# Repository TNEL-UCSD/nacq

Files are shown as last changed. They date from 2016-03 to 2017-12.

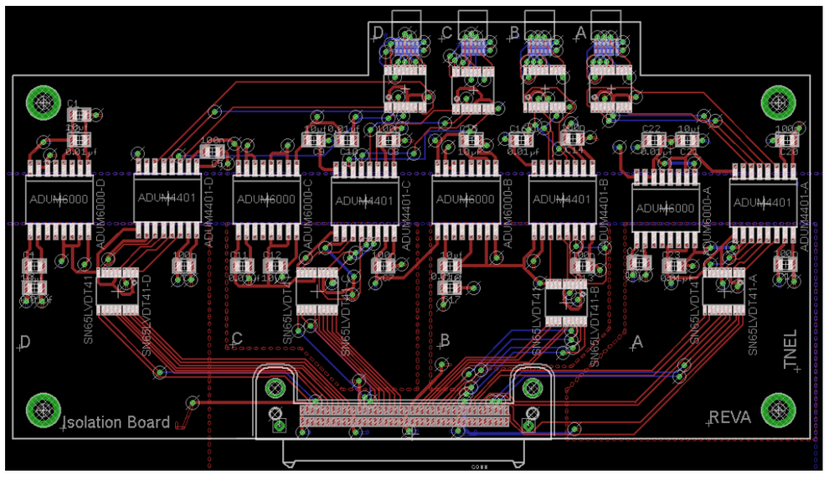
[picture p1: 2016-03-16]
cases/NACQ Case/isolation board.png

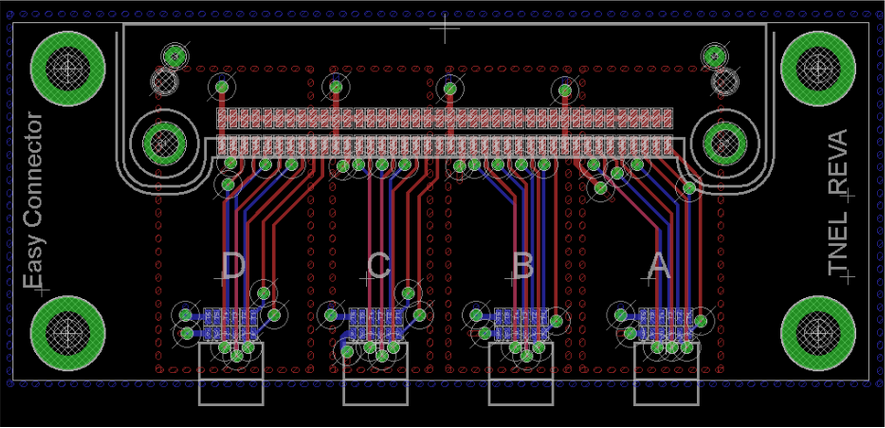
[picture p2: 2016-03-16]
cases/Easy Board Case/easy connect.png

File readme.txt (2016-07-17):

Overview:
Design files for a electrophysiology (ephys) recording tailored for the clinic. Our system is based on Intan technologies (intantech.com). 

If any of the materials are used, please cite:

J. Hermiz, N. Rogers, E. Kaestner, M. Ganji, D. Cleary, J. Snider, D. Barba, S. Dayeh, E. Halgren, V. Gilja "A clinic compatible, open source electrophysiology system." 2016 38th Annual International Conference of the IEEE Engineering in Medicine and Biology Society (EMBC). IEEE, 2016.

Included in this system are:

-Power Isolator (nacq/pcbs/Isolation Board)
-> Provides isolated power to Intan headstages. Can support up to 256 channels.

-Easy Board (nacq/pcbs/Easy Board)
-> Adapter for isolator board to intan spi cables

-Flex Adapter (nacq/pcbs/Flex Adapter)
-> Adapter that accepts flat flex cables (FFC) and plugs into headstages (RHD2132 and RHD2164)

-NACQ Case (nacq/cases/nacq)
-> Enclosure for neural acquistion hardware (power isolator and RHD2000)

-Easy Board Case (nacq/cases/Easy Board)
-> 3D printed case

Flex Adapter Case (nacq/cases/Flex Adapter)
-> 3D printed case

Intan Headstage Cases (nacq/cases/Intan Headstages)
-> 3D printed cases for RHD2164

NACQ Software (nacq/software/nacq)
-> Software to acquire and record data. Runs only on Windows 7+ systems.

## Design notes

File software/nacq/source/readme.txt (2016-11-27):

Slight changes made to intantech.com source code found on:
http://intantech.com/files/RHD2000interface_source_code_v1_5.zip

These changes allow RHD2000 USB Board to interface to the headstage through the isolators

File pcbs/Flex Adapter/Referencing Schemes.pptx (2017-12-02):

## Referencing Schemes

## Options

1. External reference
2. Device reference

## External reference

Front Side

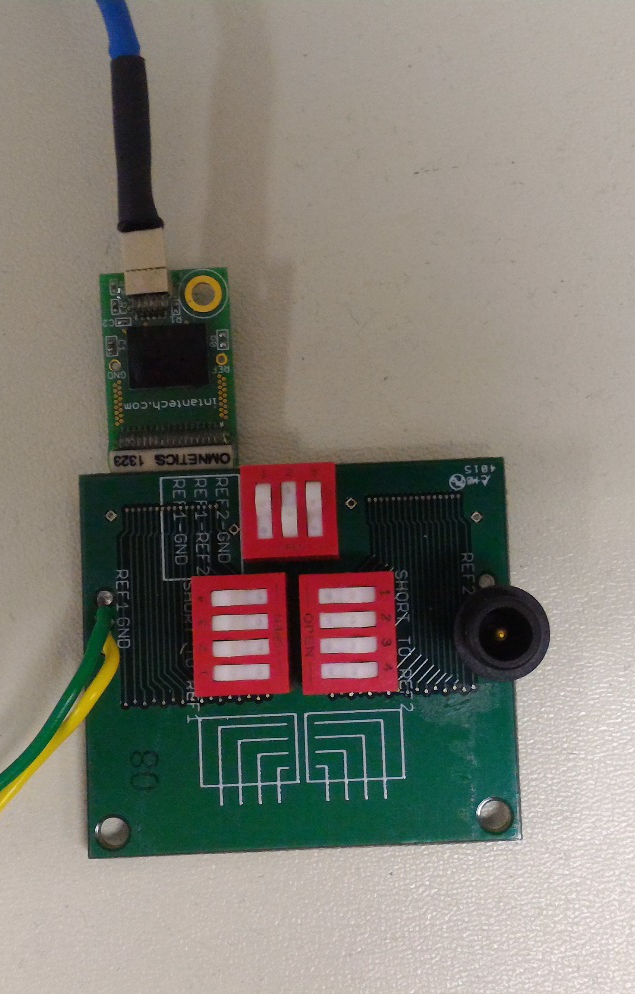
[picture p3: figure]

- Connect a needle probes to Ref1 or Ref2
- Orange circles indicate the down position of the switches
- The configuration makes it so that none of the depth electrodes are connected to reference

Intan Amplifier
64 chan

Switches

Ref and Gnd Connections

## Depth Channel Reference

Front Side

Intan Amplifier
64 chan

Switches

Ref and Gnd Connections

Back Side

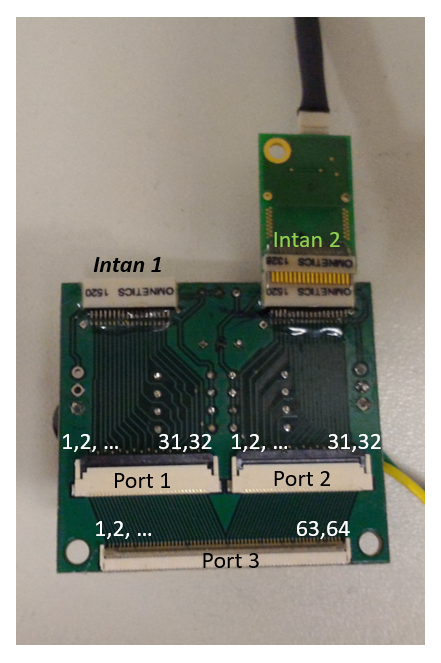
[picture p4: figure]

Macro electrode

- Ensure that the macro electrode are connected to the inner ribbon channels are indicated by the arrows
- Positions the switches are according to the orange dots

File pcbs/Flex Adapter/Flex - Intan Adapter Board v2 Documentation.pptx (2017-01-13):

## Flex - Intan Adapter Board v2

Documentation v1
John Hermiz
01/13/17

## Overview

- The objective of this document is detail the analog to software channel mapping and the switch functionality and mapping.

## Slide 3

Front Side

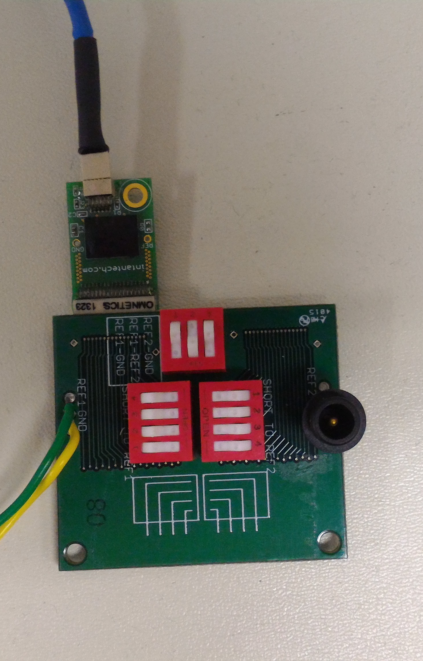
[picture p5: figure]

Back Side

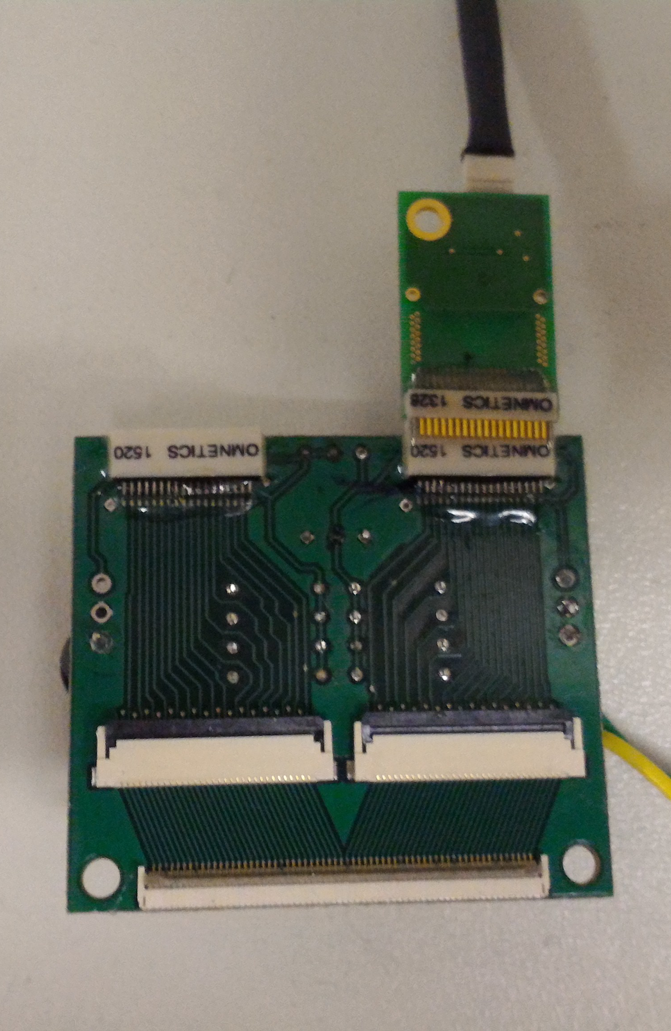
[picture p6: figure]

Intan Amplifier
64 chan

Switches

Ref and Gnd Connections

32 chan Flex Connectors

64 chan Flex Connector

Side View

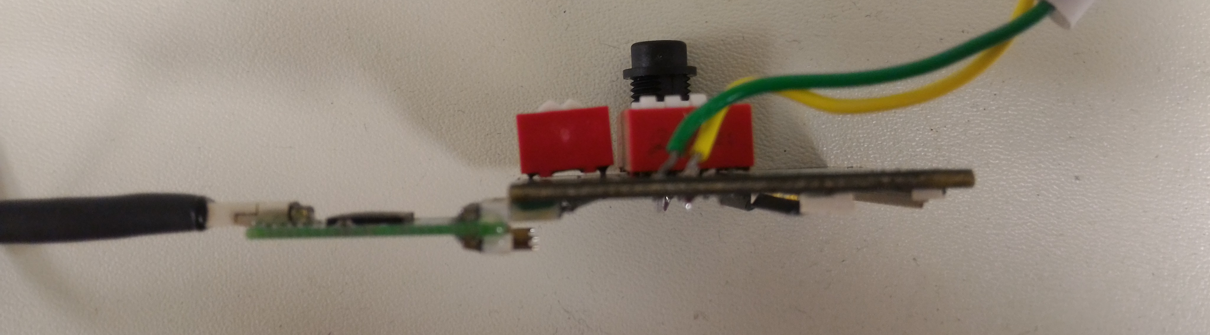
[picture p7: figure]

Front Side

Back Side

## Channel Map

1,2, … 63,64

Intan 1

Intan 2

1,2, … 31,32

1,2, … 31,32

Port 1

Port 2

Port 3

- Intan 1 is connected to Port 1
- Intan 2 is connected to Port 2
- Port 1 and Port 2 is connected to Port 3
- Note: If you use a Intan amplifier with 64 channels, then 32 channels with be unconnected since Intan 1 & 2 only accept 32 channels
- Ensure Intan Amplifiers are plugged in so that the extra pins are exposed on the back side of the board (as below)!
  - If the Intan Amplifier is plugged in the other way, then the channel map in the next slide will be wrong!

Side View

Chip Side

Front Side

Back Side

Unconnected pins

## Channel Map

1,2, … 63,64

Intan 1

Intan 2

1,2, … 31,32

1,2, … 31,32

Port 1

Port 2

Port 3

- “Channel Name” corresponds to the software channel name.
- Bold & Italicized numbers (eg. 16) corresponds to the amplifier on Intan 1
- Normal number (eg. 16) corresponds to amplifier on Intan 2

Port 1 | Port 2 | Port 3 | Channel Name
1 | - | 1 | 16
2 | - | 2 | 17
31 | - | 31 | 46
32 | - | 32 | 47
- | 1 | 33 | 17
- | 2 | 34 | 16
- | 31 | 63 | 47
- | 32 | 64 | 46

## Switches

- The switches are used to have the flexibility to short ref and gnd as well as ref to channels
- There are two refs on the board: ref1 and ref2 for each Intan amp that’s connected (there’s an option to short ref1 and ref2)
- Typically, we leave ref and gnd as separate nodes (switch is open)
- Typically, we short 2-4 channels to ref.
  - Deciding which channels to short depends on which configuration appears to eliminate noise the most

## Switches

Ref/Gnd: Group A

Switch | Function
1 (Left) | Ref 1 = GND
2 (Middle) | Ref 1 = Ref 2
3 (Right) | Ref 2 = GND

Front Side

Note: The board has 2 references nodes:
- Ref 1 (left side of board)
- Ref 2 (right side of board)

Ref/Gnd
Group A

Ref/Channel
Group BR

Ref/Gnd: Group BL

Switch | Function
1 (Bottom) | Ref 1 = 17
2 (Bottom Mid) | Ref 1 = 16
3 (Top Mid) | Ref 1 = 19
4 (Top) | Ref 1 = 18

Ref/Gnd: Group BR

Switch | Function
1 (Top) | Ref 2 = 44
2 (Top Mid) | Ref 2 = 45
3 (Bottom Mid) | Ref 2 = 46
4 (Bottom) | Ref 2 = 47

Ref/Channel
Group BL

## Switches

Front Side

Standard configuration switches prior to surgery:

Ref/Gnd: Group A

Switch | Position
1 (Left) | Open
2 (Middle) | Close
3 (Right) | Open

Ref/Gnd
Group A

Ref/Channel
Group BR

Closed switches are highlighted in orange in the figure to the right

Ref/Gnd: Group BR

Switch | Position
1 (Top) | Open
2 (Top Mid) | Open
3 (Bottom Mid) | Open or Close
4 (Bottom) | Close

Ref/Gnd: Group BL

Switch | Position
1 (Bottom) | Close
2 (Bottom Mid) | Open or Close
3 (Top Mid) | Open
4 (Top) | Open

Ref/Channel
Group BL

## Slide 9

Software Interface

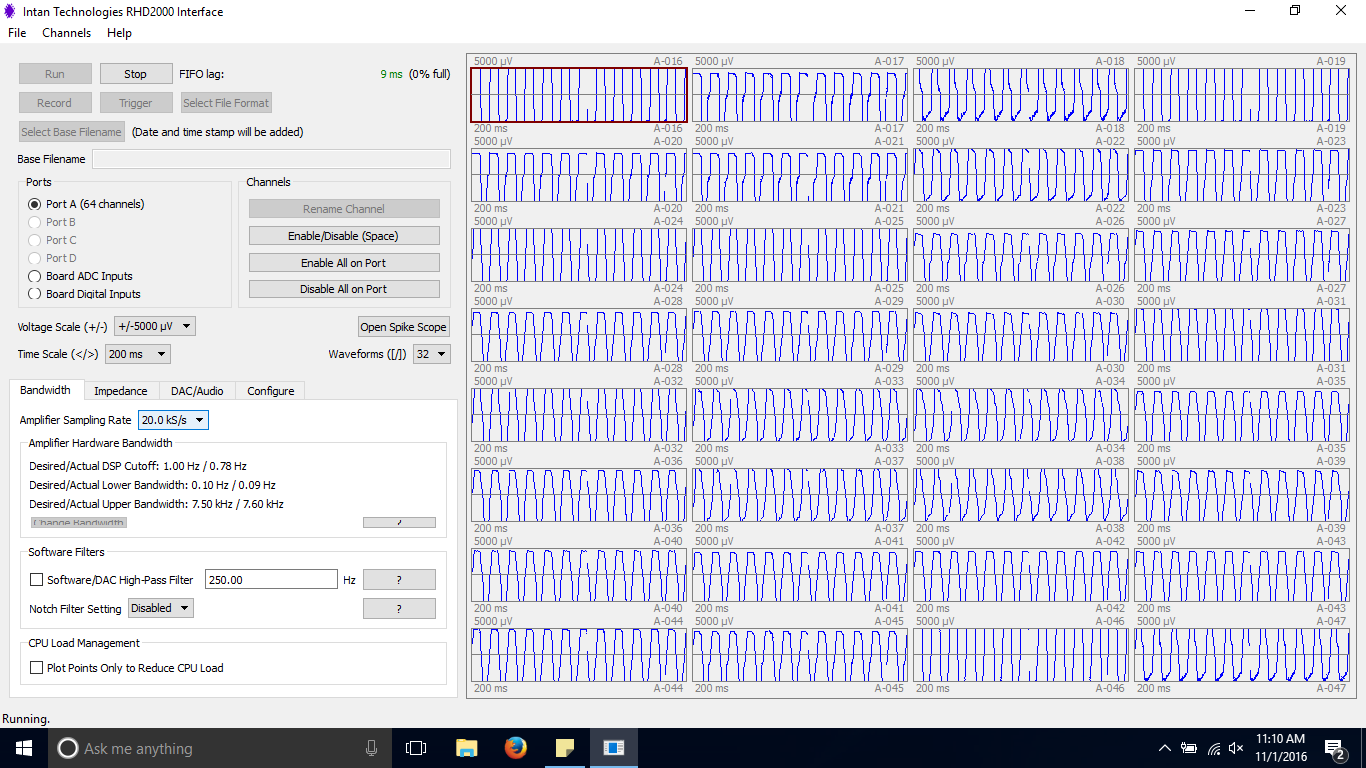
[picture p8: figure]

Channel Name

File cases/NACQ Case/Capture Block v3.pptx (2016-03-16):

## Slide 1

Top Down View

10.24

North

USB Board

Isolation Board

BNC

S

6.1

Buffer space for BNC

2.5

Buffer space for wires

~0.5

1.5

S

USB

7.09

3.9

West

4.8

P

East

S

S

S

S

2.5

2.36

SAMTEC

1.8

1

S

Ribbon

mid-line

S

P

USB

South

All dimensions are in inches. Not drawn to scale!

## Side View

Electronics Facing Up

Isolation Board

Electronics Facing Up

USB Board

## USB Board

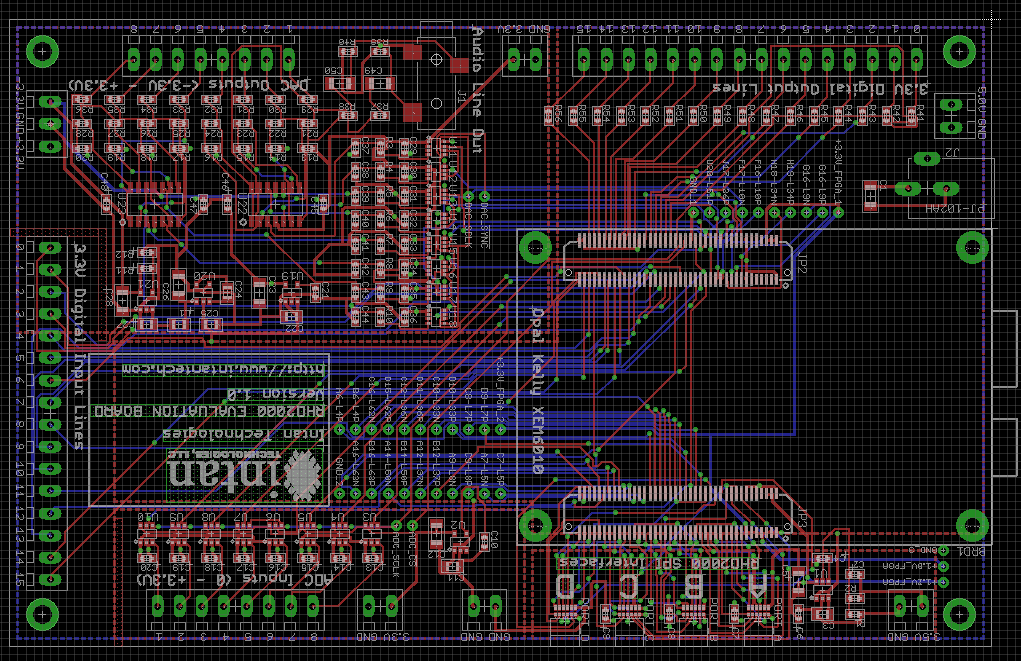
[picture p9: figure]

Screw Hole Lengths from Center to Edge

Corner | Delta X | Delta Y
NW | 200 | 200
NE | 200 | 200
SE | 200 | 200
SW | 200 | 200

USB

P

## Isolation Board

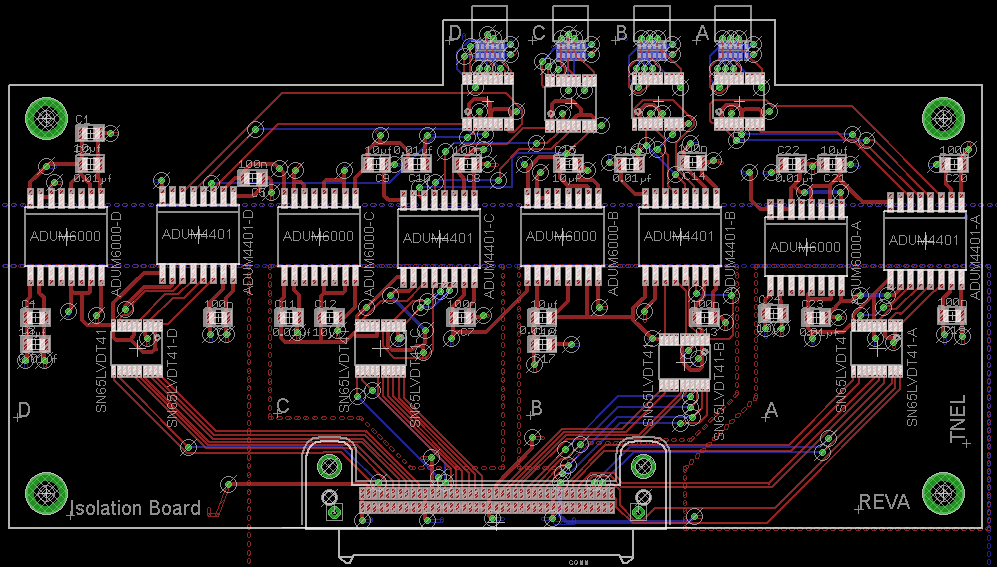
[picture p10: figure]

Have isolation board facing down (electronics facing down)

Screw Hole Lengths from Center to Edge

Corner | Delta X | Delta Y
NW | 180(4) | 166(4)
NE | 195(4) | 166(4)
SE | 195(4) | 175(4)
SW | 180(4) | 175(4)

Note: All lengths are reported in mils (thousandth of an inch), with uncertainty in (.)

## Easy Connector

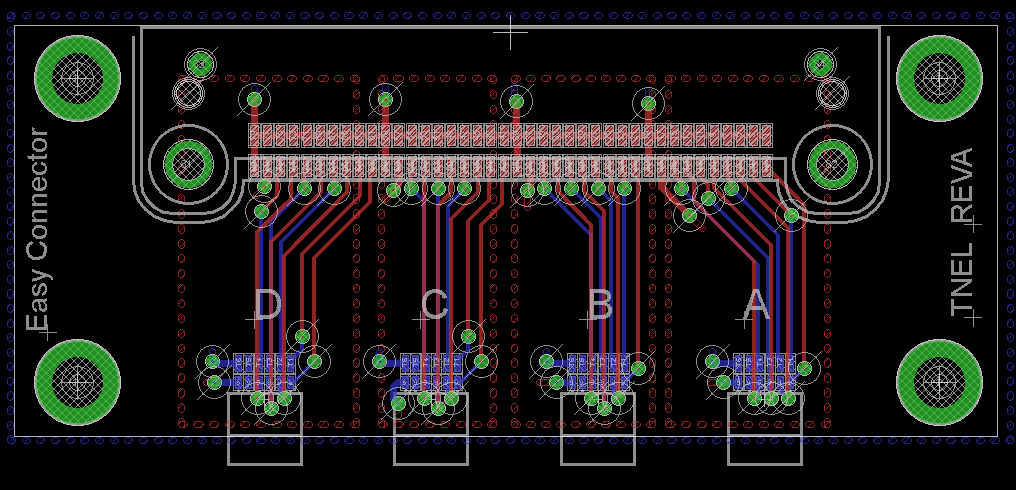
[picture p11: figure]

Screw Hole Lengths from Center to Edge

Corner | Delta X | Delta Y
NW | 150 | 127(1)
NE | 139(1) | 127(1)
SE | 139(1) | 130
SW | 150 | 130

## Capture Box 3D

South Panel View

P

USB

Ribbon Cable Slit

North Panel View

## Easy Connector 3D

SAMTEC

Ribbon Cable

## Part References/Specs

- USB Board
  - http:// (http://www.intantech.com/RHD2000_USB_interface_board.html)www.intantech.com/RHD2000_USB_interface_board.html
- Isolation Board
  - https:// (https://www.dropbox.com/sh/rtxgdsem57ctndv/AAA75mkSLeLykQKeLrcl0iwBa)www.dropbox.com/sh/rtxgdsem57ctndv/AAA75mkSLeLykQKeLrcl0iwBa
- Easy Board
  - https:// (https://www.dropbox.com/sh/qj834wxvz5nfjsx/AAAAEEapNii0fB531sr1DuTGa)www.dropbox.com/sh/qj834wxvz5nfjsx/AAAAEEapNii0fB531sr1DuTGa
- Samtec Male Connector (on Isolation Board)
  - ERM8-040-01-L-D-RA-TR
  - http:// (http://www.samtec.com/technical-specifications/Default.aspx?seriesmaster=ERM8-RA)www.samtec.com/technical-specifications/Default.aspx?seriesmaster=ERM8-RA
- Samtec Female Connector (on Easy Board)
  - ERF8-040-01-S-D-RA-TR
  - http:// (http://www.samtec.com/technical-specifications/Default.aspx?SeriesMaster=ERF8-RA)www.samtec.com/technical-specifications/Default.aspx?SeriesMaster=ERF8-RA
- Samtec Ribbon Cable
  - ERCD-010-05.00-SBR-TED-1-D
  - https:// (https://www.samtec.com/technical-specifications/Default.aspx?seriesmaster=ERCD)www.samtec.com/technical-specifications/Default.aspx?seriesmaster=ERCD
  - http:// (http://www.samtec.com/documents/webfiles/cpdf/ERCD-XXX-XX.XX-XXX-XXX-X-X-MKT.pdf)www.samtec.com/documents/webfiles/cpdf/ERCD-XXX-XX.XX-XXX-XXX-X-X-MKT.pdf
- Omnetics Connector (on USB Board, Isolation Board and Easy Board)
  - A79623-001
  - http://www.omnetics.com/polarized-nano/cots/ (http://www.omnetics.com/polarized-nano/cots/)

## Isolation Board, CPL

RefDes,Layer,LocationX,LocationY,Rotation
ADUM4401-A,Top,4.540,1.770,180
ADUM4401-B,Top,3.330,1.790,180
ADUM4401-C,Top,2.140,1.780,180
ADUM4401-D,Top,0.950,1.800,180
ADUM6000-A,Top,3.950,1.740,180
ADUM6000-B,Top,2.750,1.790,180
ADUM6000-C,Top,1.550,1.790,180
ADUM6000-D,Top,0.300,1.790,180
C1,Top,0.420,2.300,0
C2,Top,0.420,2.150,0
C3,Top,0.150,1.260,0
C4,Top,0.150,1.390,0
C5,Top,1.220,2.080,180
C6,Top,1.050,1.390,180
C7,Top,2.250,1.390,180
C8,Top,2.280,2.150,180
C9,Top,1.830,2.150,180
C10,Top,2.030,2.150,180
C11,Top,1.400,1.390,0
C12,Top,1.600,1.390,0
C13,Top,3.450,1.390,180
C14,Top,3.390,2.160,180

C15,Top,2.780,2.150,0
C16,Top,3.080,2.150,0
C17,Top,2.650,1.260,180
C18,Top,2.650,1.390,180
C19,Top,4.670,1.400,180
C20,Top,4.680,2.150,180
C21,Top,4.080,2.150,180
C22,Top,3.880,2.150,0
C23,Top,4.000,1.390,0
C24,Top,3.790,1.410,0
CONN,Top,2.420,0.380,180
OMNETICS-CONNECTOR-SLAVE-A,Bottom,3.591,2.770,0
OMNETICS-CONNECTOR-SLAVE-B,Bottom,3.191,2.770,0
OMNETICS-CONNECTOR-SLAVE-C,Bottom,2.791,2.770,0
OMNETICS-CONNECTOR-SLAVE-D,Bottom,2.391,2.770,0
SN65LVDT14-A,Top,3.620,2.460,0
SN65LVDT14-B,Top,3.220,2.460,0
SN65LVDT14-C,Top,2.790,2.450,0
SN65LVDT14-D,Top,2.380,2.460,0
SN65LVDT41-A,Top,4.300,1.240,180
SN65LVDT41-B,Top,3.350,1.170,180
SN65LVDT41-C,Top,1.850,1.240,180
SN65LVDT41-D,Top,0.650,1.240,180

## Easy Board, CPL

OMNETICS-MASTER-FPGA-A,Bottom,0.600,0.630,180
OMNETICS-MASTER-FPGA-B,Bottom,1.000,0.630,180
OMNETICS-MASTER-FPGA-C,Bottom,1.400,0.630,180
OMNETICS-MASTER-FPGA-D,Bottom,1.800,0.630,180
U$1,Top,1.190,1.510,0 “CONN”

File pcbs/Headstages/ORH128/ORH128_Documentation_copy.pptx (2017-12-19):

## ORH128

Documentation v1
John Hermiz
09/27/17

## Overview

- The objective of this document is to describe the features and details needed to operate the ORH128 board

## What is the ORH128?

ORH128 Board

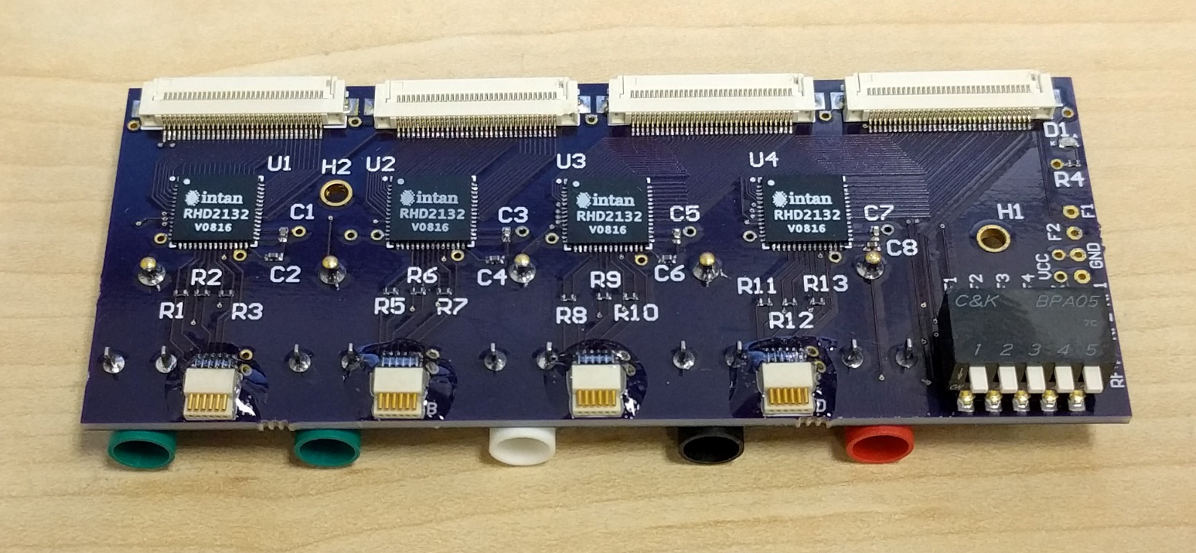
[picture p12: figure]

RHD2132

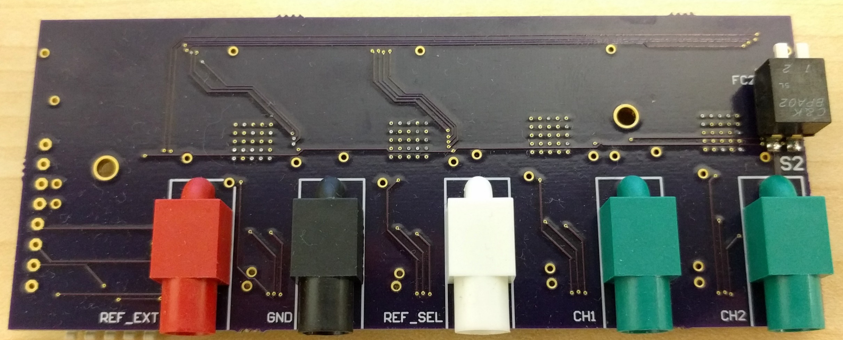
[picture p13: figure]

- It is a headstage that can record up to 128 channels of bio-potentials.
- It uses a uni-polar configuration for recording signals.
  - That is all the signals are recorded with respect to 1 reference
  - There are several options for reference
- It features four 32-channel Intan RHD2132 ASICs

Front Side

Back Side

## Inputs

- Zif Connector
  - Apply the bio-potentials to a ribbon cable, which mates with the zif connector
- Auxiliary channels
  - Two auxiliary channels are provided. These signals can be applied to the green touch proof connectors on the back side.
    - Note the switches on the back side will need to be configured so that they are passed through to the amplifier
- Reference and Ground
  - External reference and ground can be supplied to the headstage. Use the red touch proof for external reference and black for ground

## Outputs

- SPI Outputs
  - The digital outputs from the amplifer chip (RHD2132) are sent through the 12-pin omnetics connector.
    - For more details on how to communicate to RHD2132, please see Intan documentation.
    - Most users do not need to worry about this.
- Reference and Ground
  - The selected reference can be measured by connecting the white touch proof.
  - Again, ground can be accessed via the black touch proof

## Reference Switch

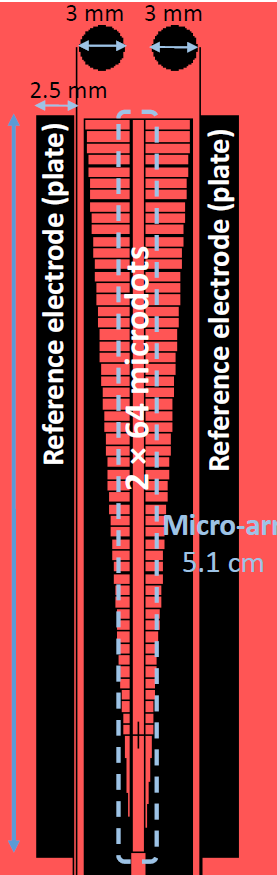
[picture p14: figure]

Ref

Ref

- To select which reference to use, configure the switches on the front side to the desired position.
- The up position means that the nodes are open and the down position means that the nodes are connected.

Reference Switch Block

Pin # | Position | Description
1 | Down | Z1 to reference
2 | Down | Z2 to reference
3 | Down | Z131 to reference
4 | Down | Z132 to reference
5 | Down | External reference to reference

Note: “reference” = REF_SEL, and “external_reference” = REF_EXT

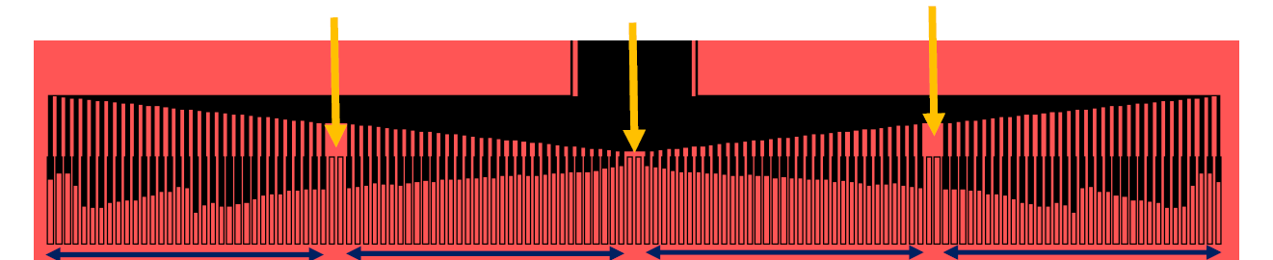
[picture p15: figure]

Z1, Z2

Z131, Z132

Pin: 1 2 3 4 5

## Auxiliary Switch

- The auxiliary switch block allows the user to connect external channels to the amplifier via the green touch proofs

Pin # | Position | Description
1 | Down | CH1 to amplifier
2 | Down | CH2 to amplifier

Pin # | Position | Description
1 | Up | Z3 to amplifier
2 | Up | Z4 to amplifier

Pin: 2 1

CH1

CH2

## Electrode Map

REF2

REF1

REF3

REF4

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
See spreadsheet for detailed mapping

REF1

RHD2132

Ports:

A

B

C

D

REF2

L1

L64

R64

R1

REF3

REF4

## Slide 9

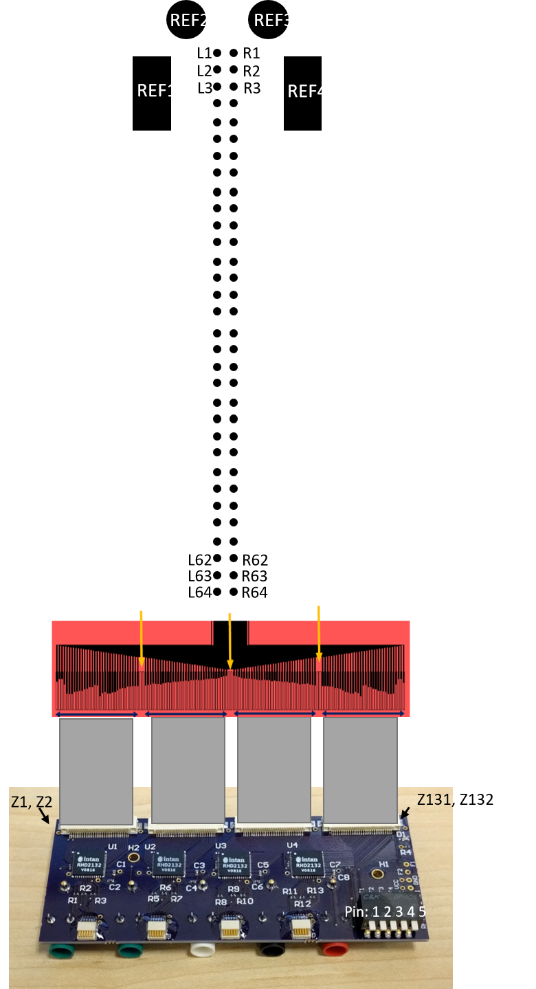
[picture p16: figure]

Origin

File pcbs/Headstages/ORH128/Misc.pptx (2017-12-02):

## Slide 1

REF2

REF1

REF3

REF4

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

Z1, Z2


Pin: 1 2 3 4 5

Z131, Z132

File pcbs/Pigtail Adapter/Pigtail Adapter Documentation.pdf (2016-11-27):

# Pigtail Adapter

Documentation v0
John Hermiz
11/7/16

## Overview

- This document describes how to use, take apart and assemble the pigtail adapter

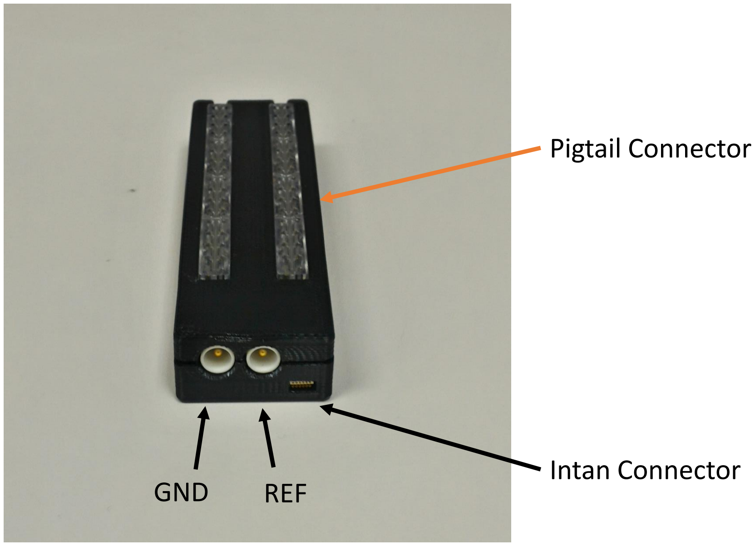
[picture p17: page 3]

Intan Connector

Pigtail Connector

GND REF

## How to Setup

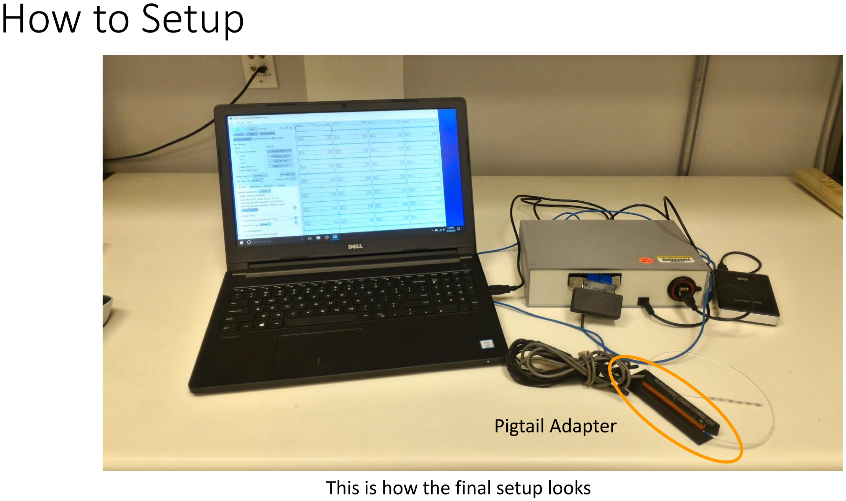
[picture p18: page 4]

This is how the final setup looks

Pigtail Adapter

## Connecting

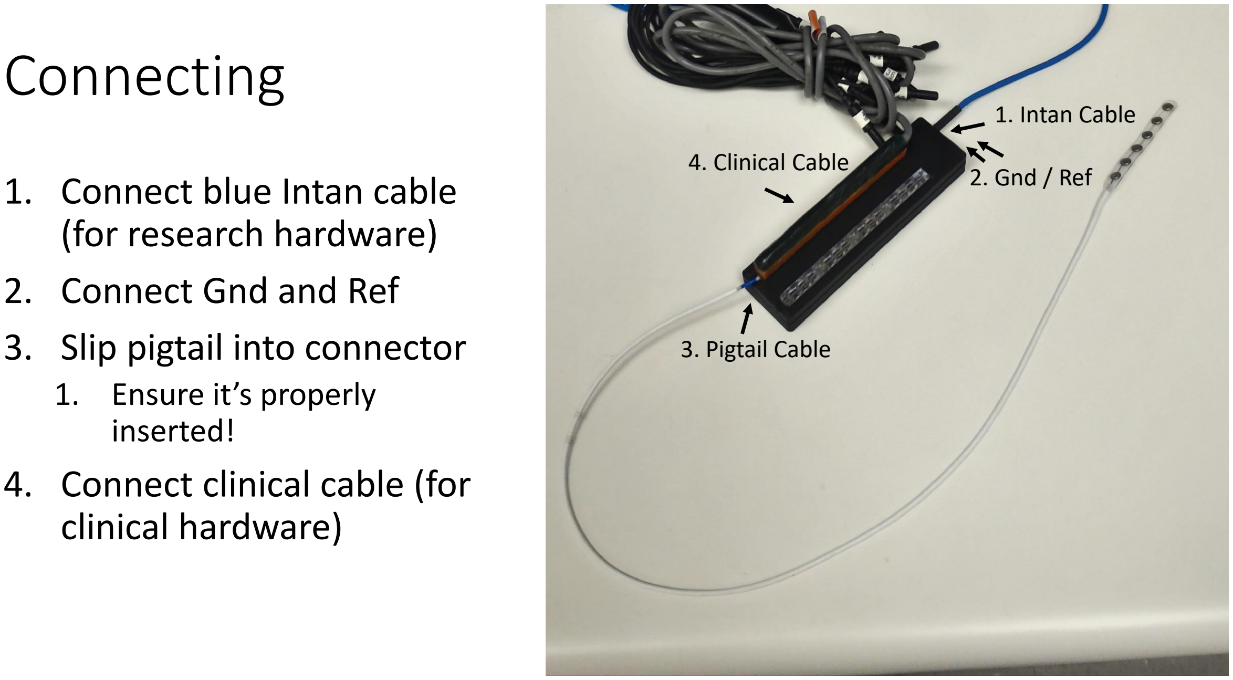
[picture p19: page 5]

1. Connect blue Intan cable (for research hardware)
2. Connect Gnd and Ref
3. Slip pigtail into connector
1. Ensure it’s properly
inserted!
4. Connect clinical cable (for clinical hardware)
1. Intan Cable
2. Gnd / Ref
3. Pigtail Cable
4. Clinical Cable

## Dis-assemble

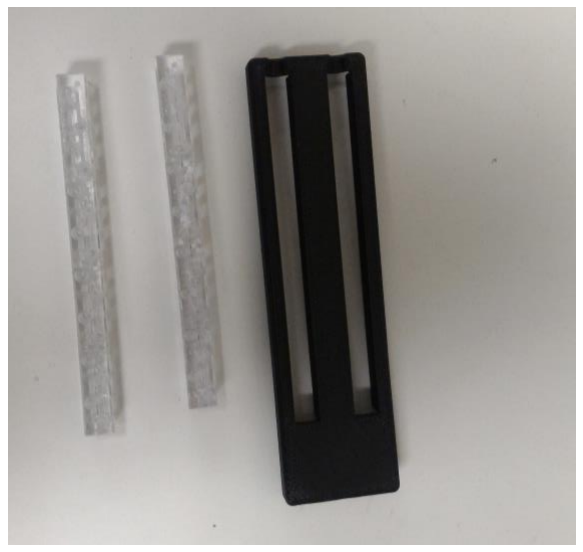
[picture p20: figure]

Pigtail Connectors can be
removed for cleaning or
replacement

WATCH DISASSEMBLE VIDEO

Written Instructions
1. Remove all connector
2. Use Philips to remove 2 screws from back
3. Pull apart back and front of case
4. Carefully pull away
electronics
5. Remove pigtail connectors by pushing them inwards

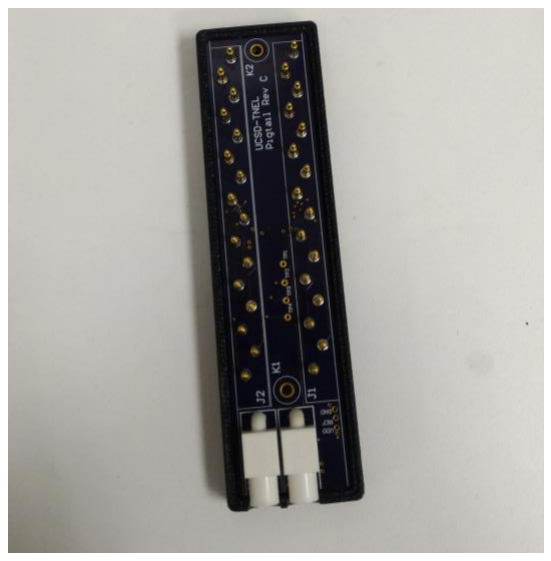
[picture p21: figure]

Electronics board

## Assemble

WATCH ASSEMBLE VIDEO

Do disassemble instructions in reverse

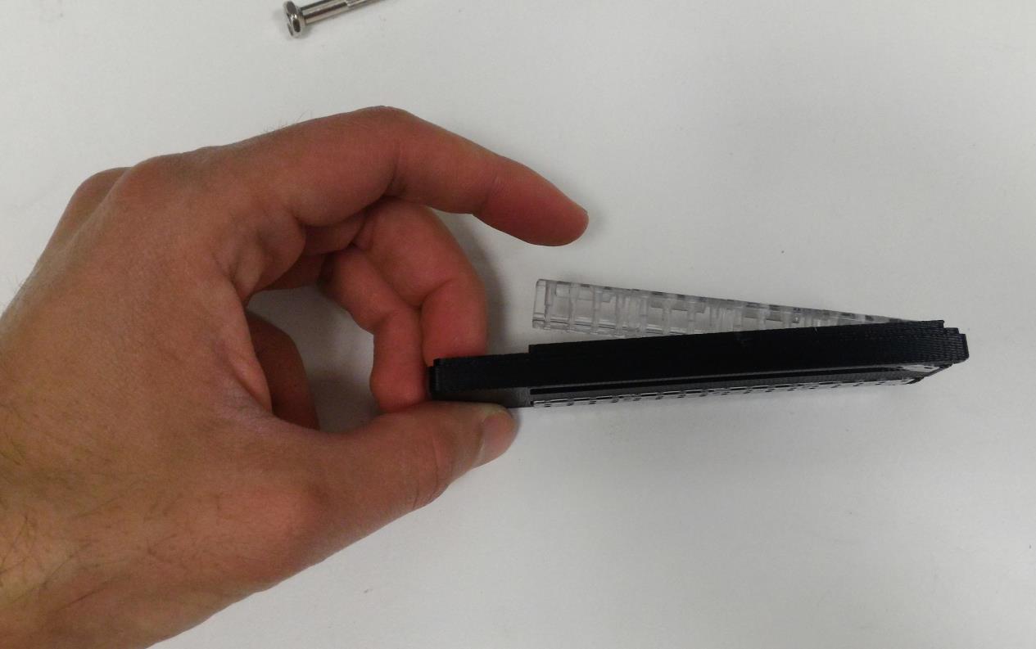
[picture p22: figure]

Push pigtail connector back into place

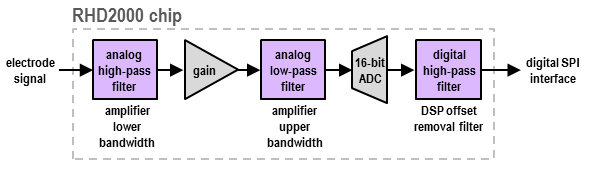
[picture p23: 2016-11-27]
software/nacq/source/images/help_diagram_chip_filters.png

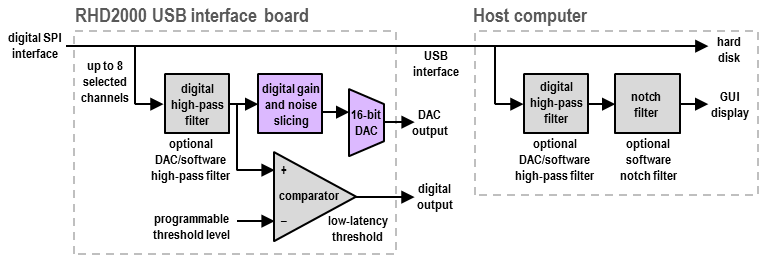
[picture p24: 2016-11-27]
software/nacq/source/images/help_diagram_DACs.png

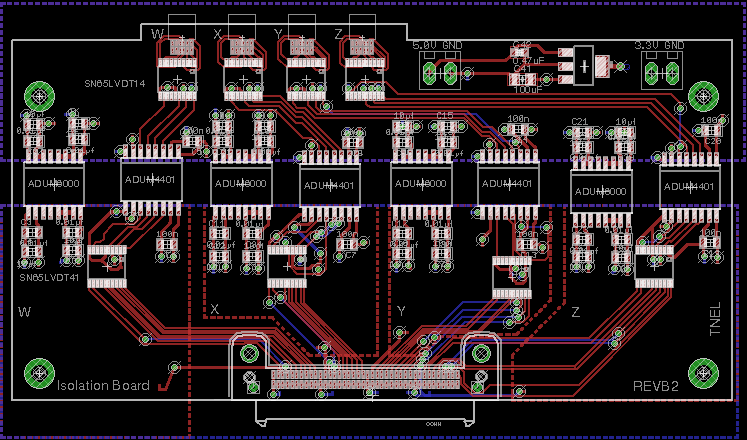
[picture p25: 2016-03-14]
pcbs/Isolation Board/isolation_board_revb2_v2.png

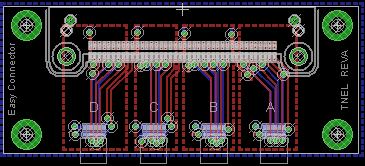
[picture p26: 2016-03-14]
pcbs/Easy Board/easy_connector_v5_auto.png

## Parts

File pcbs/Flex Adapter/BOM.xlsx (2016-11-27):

Bill of Materials |  |  | RHD2000 Electrode Adapter
Part | Quantity | Value | Device | Digi-Key part number | Notes
S1,S2 | 2 | NPD-36-AA-GS | nano strip connector | Omnetics A79024-001
C32 | 2 |  | 32-Position FFC Connector | OR724CT-ND
C64 | 1 |  | 64-Position FFC Connector | OR878CT-ND

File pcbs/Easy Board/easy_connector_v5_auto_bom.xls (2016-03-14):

Part | Value | Device | Package | Description | MPN | DIGIKEY | NON-DIGIKEY | COMMENT | COST
CONN | ERF8-040-01-D-RA | ERF8-040-01-D-RA | ERF8-040-01-D-RA | ERF8-RA | ERF8-040-05.0-S-DV-K-TR | SAM8621CT-ND |  |  | 5.65752
OMNETICS-MASTER-FPGA-A | OMNETICS-CONNECTOR-FPGA | OMNETICS-CONNECTOR-FPGA | OMNETICS_PZN-12-AA-UPDATED | 12 PIN, POLARIZED OMENTICS CONN | A79623-001 |  | OMNETICS_PZN-12-AA
OMNETICS-MASTER-FPGA-B | OMNETICS-CONNECTOR-FPGA | OMNETICS-CONNECTOR-FPGA | OMNETICS_PZN-12-AA-UPDATED | 12 PIN, POLARIZED OMENTICS CONN | A79623-001 |  | OMNETICS_PZN-12-AA
OMNETICS-MASTER-FPGA-C | OMNETICS-CONNECTOR-FPGA | OMNETICS-CONNECTOR-FPGA | OMNETICS_PZN-12-AA-UPDATED | 12 PIN, POLARIZED OMENTICS CONN | A79623-001 |  | OMNETICS_PZN-12-AA
OMNETICS-MASTER-FPGA-D | OMNETICS-CONNECTOR-FPGA | OMNETICS-CONNECTOR-FPGA | OMNETICS_PZN-12-AA-UPDATED | 12 PIN, POLARIZED OMENTICS CONN | A79623-001 |  | OMNETICS_PZN-12-AA

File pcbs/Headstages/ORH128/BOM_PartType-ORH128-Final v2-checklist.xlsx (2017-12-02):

 | Comment | Digikey# | Quantity | Designator | Footprint | LibRef | Description
R | 1e-7 F | 490-1312-1-ND | 4 | C1, C3, C5, C7 | PCB-r022o53ebngak025aow0-1 | CMP-a3286ba96bd77cef-1 | C Series 0402 0.1 uF 25 V ±10% Tolerance X5R SMT Multilayer Ceramic Capacitor
R | 1e-08 F | 445-4964-1-ND | 4 | C2, C4, C6, C8 | CAPC1005X55X25ML05T10 | CMP-118388-2 | CAP CER 10000PF 25V 10% X7R 0402
R | LED | LG L29K-F2J1-24-Z | 1 | D1 | PCB-gebjnnxoyoh522cef9yf-1 | CMP-fxk4qrf7op874518brie-1 | LG L29K-F2J1-24-Z
N/A | Testpoint | N/A | 8 | F1, F2, GND, RF1, RF2, RF3, RF4, VCC | PCB-wowtwtb07sxbfxs0ky84-1 | CMP-pszd58k1v19geaubrh38-4 | Thru Hole
N/A | Screw Hole, D = 2.438 mm | N/A | 2 | H1, H2 | PCB-hb9vn33d8jvzkdbrvr5y-1 | CMP-8emc2svkljyrgsbpsz1l-2 | Screw Hole, Diameter 2.438 mm
R | TE Connectivity / AMP 3-1775333-3 | A120672CT-ND | 4 | J1, J2, J3, J4 | PCB-l13sups9l195yeww75mc-1 | CMP-60c3ab186a2abf04-2 | A120672CT-ND
R | Omnetics PZN-12-AA | N/A | 4 | J5, J6, J7, J8 | PCB-q0y0p00g06q500ub6par-1 | CMP-uaq8b4blouydrnlwed2j-2 | 12 POS, SMT
R | 41828 PlasticsOne | N/A | 5 | J9, J10, J11, J12, J13 | PCBComponent_1 - duplicate | CMP-h1xkc8h7cebi3it0cn10-11 | 41828 PlasticsOne touchproof connector
R | 100.0 O | P100JCT-ND | 12 | R1, R2, R3, R5, R6, R7, R8, R9, R10, R11, R12, R13 | RESC1005X40X25NL05T05 | CMP-1846654-2 | Res Thick Film 0402 100 Ohm 5% 0.1W(1/10W) ±200ppm/C Molded SMD Automotive Punched T/R
R | 1.00 kO | 541-1.00KLCT-ND | 1 | R4 | PCB-mymoq88mns0e2su8iqhl-1 | CMP-1856342-8 | Resistor; Thick Film; 1 Kilohms; 0.063 W; 1%; SMT; 0402; TCR 37 ppm/DegC; Tape and Reel
R | C&K Components BPA05SB | CKN6143-ND | 1 | S1 | PCB-01sjs0mf2xmclz1rwdxo-1 | CMP-28f6e19bcf70f731-4 | Slide Switch, RIGHT ANGLE, Number Of Positions: 5, SURFACE MOUNT Terminal, PCB Hole Count: 10
R | C&K Components BPA02SB | CKN6139-ND | 1 | S2 | PCB-lb92s550mxt6ppqr28vc-1 | CMP-2035e92f00ecfff2-1 | Slide Switch, RIGHT ANGLE, Number Of Positions: 2, SURFACE MOUNT Terminal, PCB Hole C
 | RHD2132 | N/A | 4 | U1, U2, U3, U4 | PCB-j18u5jfj1j6gc9wn5fw3-1 | CMP-2edc1jpem0idcrnv700k-3 | Intan 32 Channel A/D

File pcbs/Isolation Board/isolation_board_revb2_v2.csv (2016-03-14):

Part | Value | Device | Package | Description | MPN | DIGIKEY
ADUM4401-W | ADUM4401 | ADUM4401 | SOIC16R | IC DGTL ISO 4CH LOGIC 16SOIC | ADUM4401CRWZ | ADUM4401CRWZ-ND
ADUM4401-X | ADUM4401 | ADUM4401 | SOIC16R | IC DGTL ISO 4CH LOGIC 16SOIC | ADUM4401CRWZ | ADUM4401CRWZ-ND
ADUM4401-Y | ADUM4401 | ADUM4401 | SOIC16R | IC DGTL ISO 4CH LOGIC 16SOIC | ADUM4401CRWZ | ADUM4401CRWZ-ND
ADUM4401-Z | ADUM4401 | ADUM4401 | SOIC16R | IC DGTL ISO 4CH LOGIC 16SOIC | ADUM4401CRWZ | ADUM4401CRWZ-ND
ADUM6000-W | ADUM6000 | ADUM6000 | SOIC16R | ISOL DC-DC CONV 5KVRMS 16SOIC W | ADUM6000ARWZ | ADUM6000ARWZ-ND
ADUM6000-X | ADUM6000 | ADUM6000 | SOIC16R | ISOL DC-DC CONV 5KVRMS 16SOIC W | ADUM6000ARWZ | ADUM6000ARWZ-ND
ADUM6000-Y | ADUM6000 | ADUM6000 | SOIC16R | ISOL DC-DC CONV 5KVRMS 16SOIC W | ADUM6000ARWZ | ADUM6000ARWZ-ND
ADUM6000-Z | ADUM6000 | ADUM6000 | SOIC16R | ISOL DC-DC CONV 5KVRMS 16SOIC W | ADUM6000ARWZ | ADUM6000ARWZ-ND
R1 | 0.01ohm | R_0603 | 603 | RES 0.01 OHM 1/4W 1% 0603 SMD | PMR03EZPFU10L0 | RHM0.01BVCT-ND
R2 | 0.01ohm | R_0603 | 603 | RES 0.01 OHM 1/4W 1% 0603 SMD | PMR03EZPFU10L0 | RHM0.01BVCT-ND
R3 | 0.01ohm | R_0603 | 603 | RES 0.01 OHM 1/4W 1% 0603 SMD | PMR03EZPFU10L0 | RHM0.01BVCT-ND
R4 | 0.01ohm | R_0603 | 603 | RES 0.01 OHM 1/4W 1% 0603 SMD | PMR03EZPFU10L0 | RHM0.01BVCT-ND
R5 | 0.01ohm | R_0603 | 603 | RES 0.01 OHM 1/4W 1% 0603 SMD | PMR03EZPFU10L0 | RHM0.01BVCT-ND
C1 | 10µf | C_0805 | 805 | CAP CER 10UF 10V Y5V 0805 | CC0805ZKY5V6BB106 | 311-1355-1-ND
C2 | 0.01µf | C_0805 | 805 | CAP CER 10000PF 50V Y5V 0805 | GRM216F51H103ZA01D | 490-1720-1-ND
C3 | 0.01µf | C_0805 | 805 | CAP CER 10000PF 50V Y5V 0805 | GRM216F51H103ZA01D | 490-1720-1-ND
C4 | 10µf | C_0805 | 805 | CAP CER 10UF 10V Y5V 0805 | CC0805ZKY5V6BB106 | 311-1355-1-ND
C5 | 100n | C_0805 | 805 | CAP CER 0.1UF 50V Y5V 0805 | CL21F104ZBCNNNC | 1276-1007-1-ND
C6 | 100n | C_0805 | 805 | CAP CER 0.1UF 50V Y5V 0805 | CL21F104ZBCNNNC | 1276-1007-1-ND
C7 | 100n | C_0805 | 805 | CAP CER 0.1UF 50V Y5V 0805 | CL21F104ZBCNNNC | 1276-1007-1-ND
C8 | 100n | C_0805 | 805 | CAP CER 0.1UF 50V Y5V 0805 | CL21F104ZBCNNNC | 1276-1007-1-ND
C9 | 10µf | C_0805 | 805 | CAP CER 10UF 10V Y5V 0805 | CC0805ZKY5V6BB106 | 311-1355-1-ND
C10 | 0.01µf | C_0805 | 805 | CAP CER 10000PF 50V Y5V 0805 | GRM216F51H103ZA01D | 490-1720-1-ND
C11 | 0.01µf | C_0805 | 805 | CAP CER 10000PF 50V Y5V 0805 | GRM216F51H103ZA01D | 490-1720-1-ND
C12 | 10µf | C_0805 | 805 | CAP CER 10UF 10V Y5V 0805 | CC0805ZKY5V6BB106 | 311-1355-1-ND
C13 | 100n | C_0805 | 805 | CAP CER 0.1UF 50V Y5V 0805 | CL21F104ZBCNNNC | 1276-1007-1-ND
C14 | 100n | C_0805 | 805 | CAP CER 0.1UF 50V Y5V 0805 | CL21F104ZBCNNNC | 1276-1007-1-ND
C15 | 10µf | C_0805 | 805 | CAP CER 10UF 10V Y5V 0805 | CC0805ZKY5V6BB106 | 311-1355-1-ND
C16 | 0.01µf | C_0805 | 805 | CAP CER 10000PF 50V Y5V 0805 | GRM216F51H103ZA01D | 490-1720-1-ND
C17 | 0.01µf | C_0805 | 805 | CAP CER 10000PF 50V Y5V 0805 | GRM216F51H103ZA01D | 490-1720-1-ND
C18 | 10µf | C_0805 | 805 | CAP CER 10UF 10V Y5V 0805 | CC0805ZKY5V6BB106 | 311-1355-1-ND
C19 | 100n | C_0805 | 805 | CAP CER 0.1UF 50V Y5V 0805 | CL21F104ZBCNNNC | 1276-1007-1-ND
C20 | 100n | C_0805 | 805 | CAP CER 0.1UF 50V Y5V 0805 | CL21F104ZBCNNNC | 1276-1007-1-ND
C21 | 10µf | C_0805 | 805 | CAP CER 10UF 10V Y5V 0805 | CC0805ZKY5V6BB106 | 311-1355-1-ND
C22 | 0.01µf | C_0805 | 805 | CAP CER 10000PF 50V Y5V 0805 | GRM216F51H103ZA01D | 490-1720-1-ND
C23 | 0.01µf | C_0805 | 805 | CAP CER 10000PF 50V Y5V 0805 | GRM216F51H103ZA01D | 490-1720-1-ND
C24 | 10µf | C_0805 | 805 | CAP CER 10UF 10V Y5V 0805 | CC0805ZKY5V6BB106 | 311-1355-1-ND
C25 | 10µf | C_0805 | 805 | CAP CER 10UF 10V Y5V 0805 | CC0805ZKY5V6BB106 | 311-1355-1-ND
C26 | 0.01µf | C_0805 | 805 | CAP CER 10000PF 50V Y5V 0805 | GRM216F51H103ZA01D | 490-1720-1-ND
C27 | 0.01µf | C_0805 | 805 | CAP CER 10000PF 50V Y5V 0805 | GRM216F51H103ZA01D | 490-1720-1-ND
C28 | 10µf | C_0805 | 805 | CAP CER 10UF 10V Y5V 0805 | CC0805ZKY5V6BB106 | 311-1355-1-ND
C29 | 10µf | C_0805 | 805 | CAP CER 10UF 10V Y5V 0805 | CC0805ZKY5V6BB106 | 311-1355-1-ND
C30 | 0.01µf | C_0805 | 805 | CAP CER 10000PF 50V Y5V 0805 | GRM216F51H103ZA01D | 490-1720-1-ND
C31 | 0.01µf | C_0805 | 805 | CAP CER 10000PF 50V Y5V 0805 | GRM216F51H103ZA01D | 490-1720-1-ND
C32 | 10µf | C_0805 | 805 | CAP CER 10UF 10V Y5V 0805 | CC0805ZKY5V6BB106 | 311-1355-1-ND
C33 | 10µf | C_0805 | 805 | CAP CER 10UF 10V Y5V 0805 | CC0805ZKY5V6BB106 | 311-1355-1-ND
C34 | 0.01µf | C_0805 | 805 | CAP CER 10000PF 50V Y5V 0805 | GRM216F51H103ZA01D | 490-1720-1-ND
C35 | 0.01µf | C_0805 | 805 | CAP CER 10000PF 50V Y5V 0805 | GRM216F51H103ZA01D | 490-1720-1-ND
C36 | 10µf | C_0805 | 805 | CAP CER 10UF 10V Y5V 0805 | CC0805ZKY5V6BB106 | 311-1355-1-ND
C37 | 10µf | C_0805 | 805 | CAP CER 10UF 10V Y5V 0805 | CC0805ZKY5V6BB106 | 311-1355-1-ND
C38 | 0.01µf | C_0805 | 805 | CAP CER 10000PF 50V Y5V 0805 | GRM216F51H103ZA01D | 490-1720-1-ND
C39 | 0.01µf | C_0805 | 805 | CAP CER 10000PF 50V Y5V 0805 | GRM216F51H103ZA01D | 490-1720-1-ND
C40 | 10µf | C_0805 | 805 | CAP CER 10UF 10V Y5V 0805 | CC0805ZKY5V6BB106 | 311-1355-1-ND
C41 | 100uF | C_1206 | 1206 | CAP CER 100UF 10V 20% X5R 1206 | C3216X5R1A107M160AC | 445-6007-1-ND
C42 | 0.47uF | C_0402 | 402 | CAP CER 0.47UF 10V 10% X5R 0402 | LMK105BJ474KV-F | 587-1455-1-ND
CONN | ERM8-040-01-L-D-RA-TR | ERM8-040-01-L-D-RA-TR | ERM8-040-01-L-D-RA-TR | ERM8-040-01-L-D-RA-TR | ERM8-040-01-L-D-RA-TR
OMNETICS-CONNECTOR-SLAVE-W | OMNETICS-CONNECTOR-SLAVE-SIDE | OMNETICS-CONNECTOR-SLAVE-SIDE | OMNETICS_PZN-12-AA-UPDATED | A79623-001 | OMNETICS_PZN-12-AA
OMNETICS-CONNECTOR-SLAVE-X | OMNETICS-CONNECTOR-SLAVE-SIDE | OMNETICS-CONNECTOR-SLAVE-SIDE | OMNETICS_PZN-12-AA-UPDATED | A79623-001 | OMNETICS_PZN-12-AA
OMNETICS-CONNECTOR-SLAVE-Y | OMNETICS-CONNECTOR-SLAVE-SIDE | OMNETICS-CONNECTOR-SLAVE-SIDE | OMNETICS_PZN-12-AA-UPDATED | A79623-001 | OMNETICS_PZN-12-AA
OMNETICS-CONNECTOR-SLAVE-Z | OMNETICS-CONNECTOR-SLAVE-SIDE | OMNETICS-CONNECTOR-SLAVE-SIDE | OMNETICS_PZN-12-AA-UPDATED | A79623-001 | OMNETICS_PZN-12-AA
S1 | TERMINAL_BLOCK_2-3.5MM-3.3V | TERMINAL_BLOCK_2-3.5MM-3.3V | TERMINAL_BLOCK_3.5MM_2_3.3V | TERMINAL BLOCK 3.5MM 2POS PCB | ED555/2DS | ED1514-ND
S2 | TERMINAL_BLOCK_2-3.5MM-3.3V | TERMINAL_BLOCK_2-3.5MM-3.3V | TERMINAL_BLOCK_3.5MM_2_3.3V | TERMINAL BLOCK 3.5MM 2POS PCB | ED555/2DS | ED1514-ND
SN65LVDT41-W | SN65LVDT41 | SN65LVDT41UPDATED | SN65LVDT41-UPDATED | IC DIFF LINE 1DVR/4RCVR 20TSSOP | SN65LVDT41QPWREP | 296-21246-1-ND
SN65LVDT41-X | SN65LVDT41 | SN65LVDT41UPDATED | SN65LVDT41-UPDATED | IC DIFF LINE 1DVR/4RCVR 20TSSOP | SN65LVDT41QPWREP | 296-21246-1-ND
SN65LVDT41-Y | SN65LVDT41 | SN65LVDT41UPDATED | SN65LVDT41-UPDATED | IC DIFF LINE 1DVR/4RCVR 20TSSOP | SN65LVDT41QPWREP | 296-21246-1-ND
SN65LVDT41-Z | SN65LVDT41 | SN65LVDT41UPDATED | SN65LVDT41-UPDATED | IC DIFF LINE 1DVR/4RCVR 20TSSOP | SN65LVDT41QPWREP | 296-21246-1-ND
SNDLVDT14-W | SN65LVDT14 | SN65LVDT14 | SN65LDVT14 | IC LVDS 4DRVR/1RCVR 20-TSSOP | SN65LVDT14QPWREP | 296-19499-1-ND
SNDLVDT14-X | SN65LVDT14 | SN65LVDT14 | SN65LDVT14 | IC LVDS 4DRVR/1RCVR 20-TSSOP | SN65LVDT14QPWREP | 296-19499-1-ND
SNDLVDT14-Y | SN65LVDT14 | SN65LVDT14 | SN65LDVT14 | IC LVDS 4DRVR/1RCVR 20-TSSOP | SN65LVDT14QPWREP | 296-19499-1-ND
SNDLVDT14-Z | SN65LVDT14 | SN65LVDT14 | SN65LDVT14 | IC LVDS 4DRVR/1RCVR 20-TSSOP | SN65LVDT14QPWREP | 296-19499-1-ND
U1 | LM3940IMP-3.3 | LM3940IMP-3.3 | SOT223 | 1A Low Dropout Regulator for 5V to 3.3V Conversion | LM3940IMP-3.3/NOPB | LM3940IMP-3.3/NOPBCT-ND

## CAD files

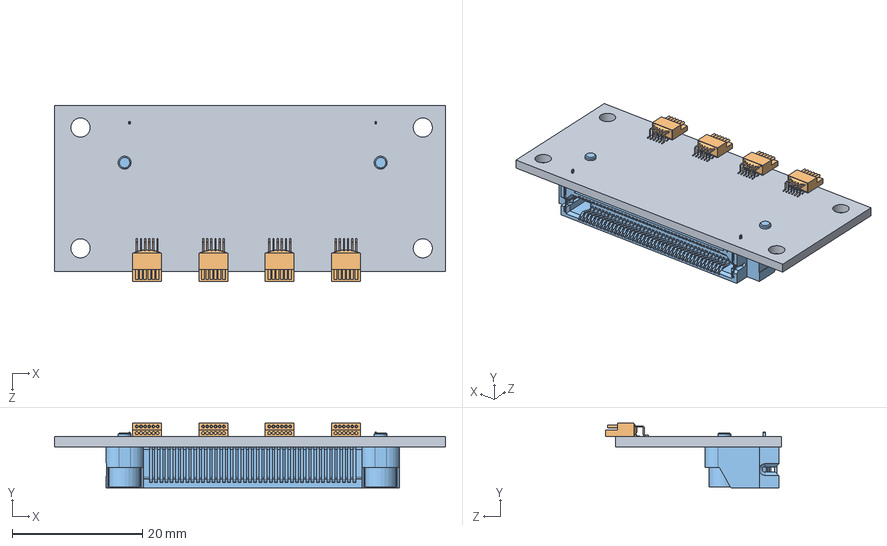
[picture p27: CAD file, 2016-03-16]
cases/Easy Board Case/easy connector board asm.SLDASM
59.9 x 9.91 x 26.9 mm
easy connector board
A79623-001 x 4
samtec female

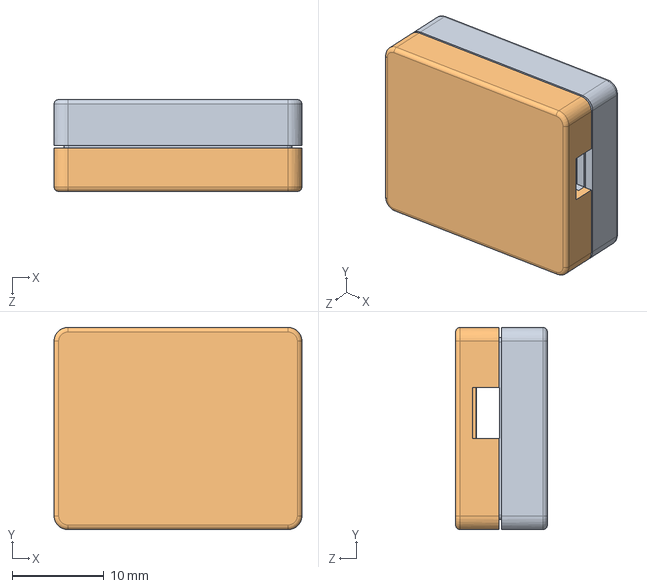
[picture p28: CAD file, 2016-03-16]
cases/Intan Headstage Case/Intan RHD2164 Case Compact/electrical enclosure.sldasm
27.0 x 22.0 x 10.0 mm
Mirror5

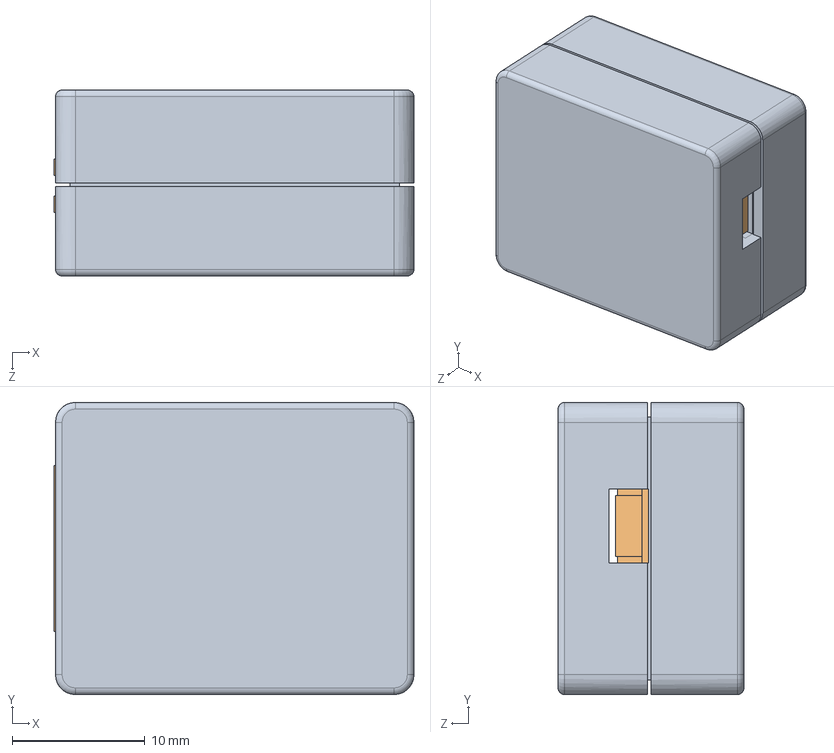
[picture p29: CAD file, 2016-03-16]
cases/Intan Headstage Case/Intan RHD2164 Case/Assem1.SLDASM
27.1 x 22.0 x 14.0 mm
connector enclosure
connector board

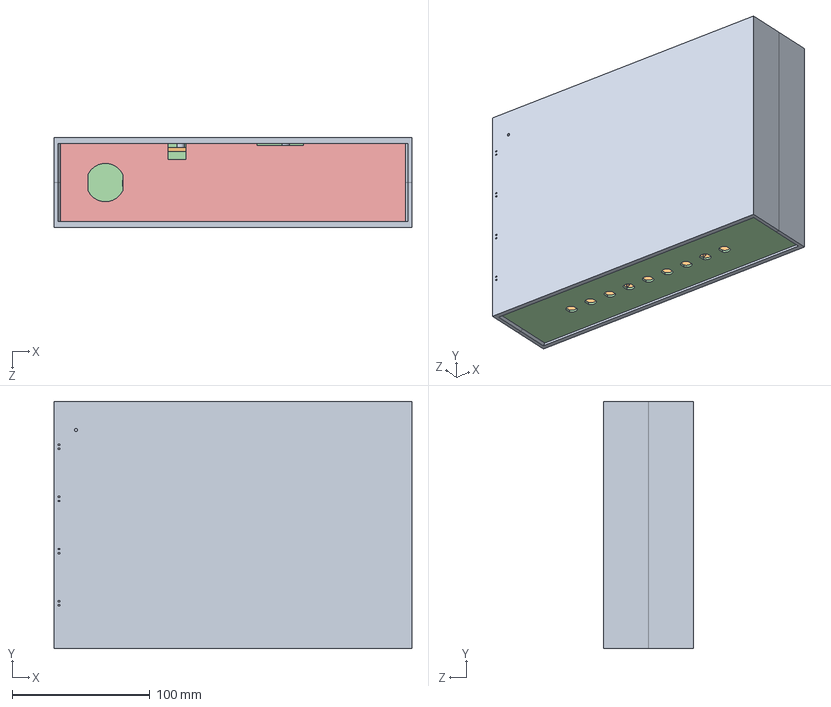
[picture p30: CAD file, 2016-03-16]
cases/NACQ Case/box asm.SLDASM
260.1 x 179.7 x 65.1 mm
box base 3D x 2
USB plate
isolation plate
side panel bnc
side panel ribbon power usb
isolation board
Samtec-ERM8-040-01-L-D-RA

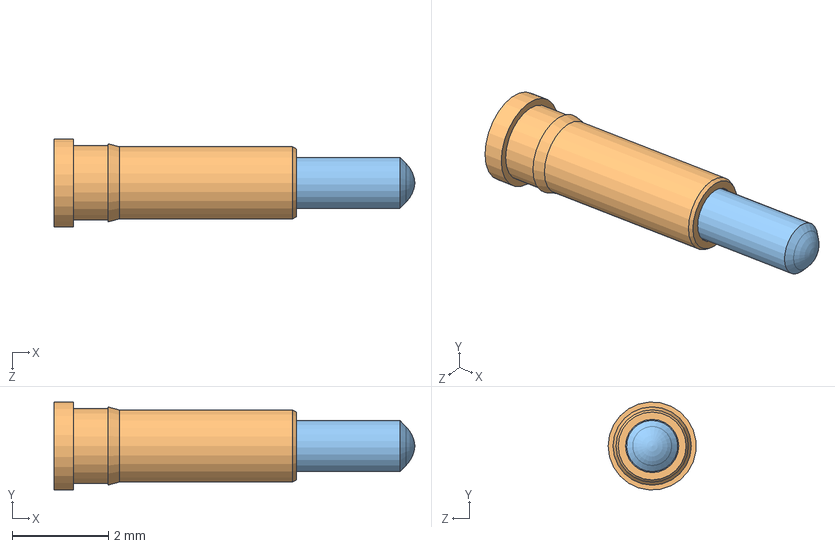
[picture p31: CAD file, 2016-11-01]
cases/Pigtail Adapter Case/mill-max-0928-0-15-20-77-14-11-0/mill-max-0928-0-15-20-77-14-11-0.sldasm
7.49 x 1.83 x 1.82 mm
mill-max-0928-0-15-20-77-14-11-0_0960-X
mill-max-0928-0-15-20-77-14-11-0_6958-0
mill-max-0928-0-15-20-77-14-11-0_6914-0
mill-max-0928-0-15-20-77-14-11-0_SPRING

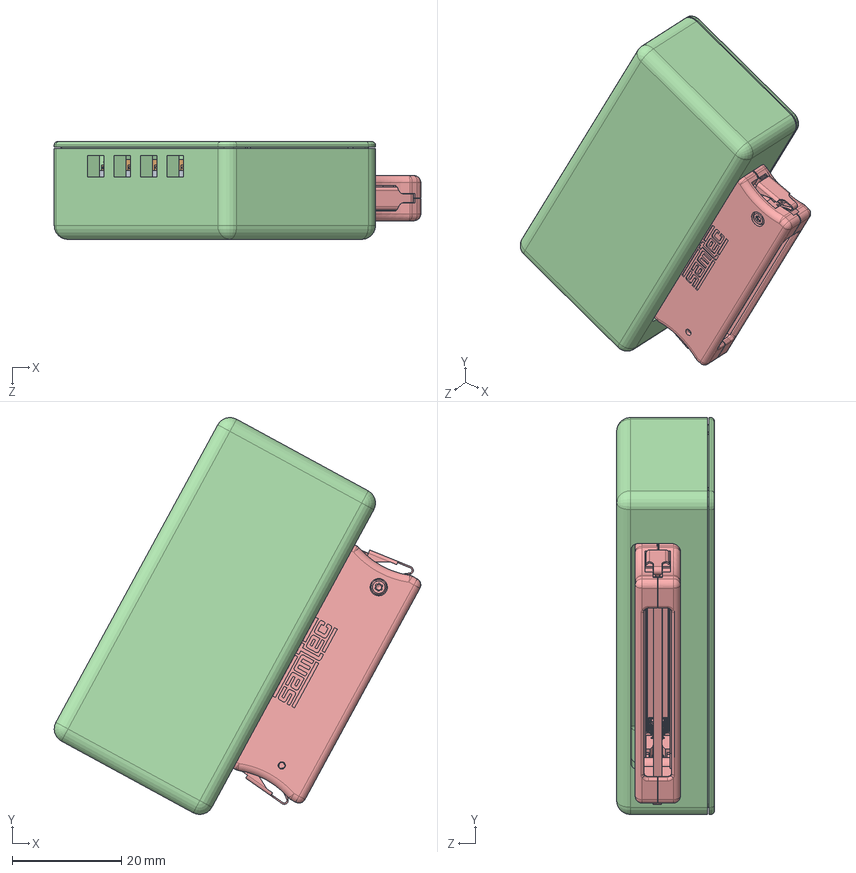
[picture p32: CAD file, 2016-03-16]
cases/Easy Board Case/easy connector fit assmebly.SLDASM
67.1 x 72.6 x 17.9 mm
easy connector board
A79623-001 x 4
samtec female
easy connector box
ted connector

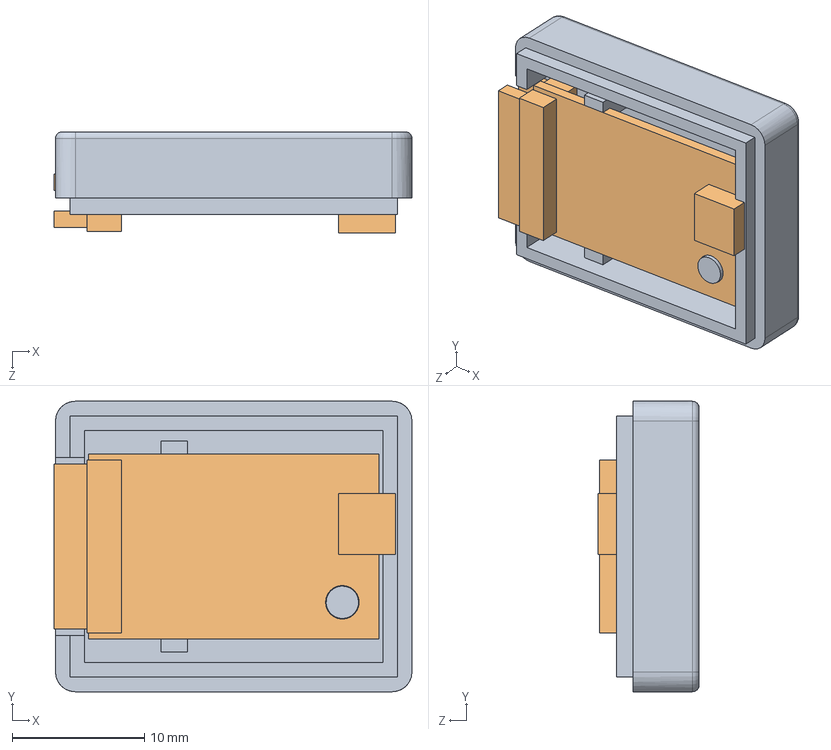
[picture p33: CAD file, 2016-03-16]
cases/Intan Headstage Case/Intan RHD2164 Case Compact/Assem1.SLDASM
27.1 x 22.0 x 7.68 mm
connector enclosure
connector board

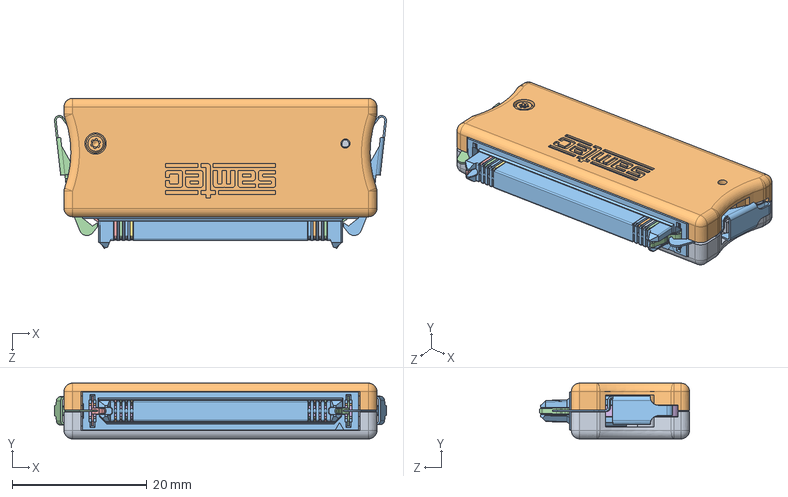
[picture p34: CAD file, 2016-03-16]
cases/NACQ Case/ted connector.SLDASM
49.3 x 8.29 x 22.3 mm
ERCD-040-TED-S-1-1
ERCD-040-TED-S-1-2
ERCD-040-TED-S-1-3
ERCD-040-TED-S-1-4
ERCD-040-TED-S-1-5
ERCD-040-TED-S-1-6
ERCD-040-TED-S-1-7
ERCD-040-TED-S-1-8
ERCD-040-TED-S-1-9
ERCD-040-TED-S-1-10
ERCD-040-TED-S-1-11
ERCD-040-TED-S-1-12
ERCD-040-TED-S-1-13
ERCD-040-TED-S-1-14
ERCD-040-TED-S-1-15
ERCD-040-TED-S-1-16
ERCD-040-TED-S-1-17
ERCD-040-TED-S-1-18
ERCD-040-TED-S-1-19
ERCD-040-TED-S-1-20
ERCD-040-TED-S-1-21
ERCD-040-TED-S-1-22
ERCD-040-TED-S-1-23
ERCD-040-TED-S-1-24
ERCD-040-TED-S-1-25
ERCD-040-TED-S-1-26
ERCD-040-TED-S-1-27

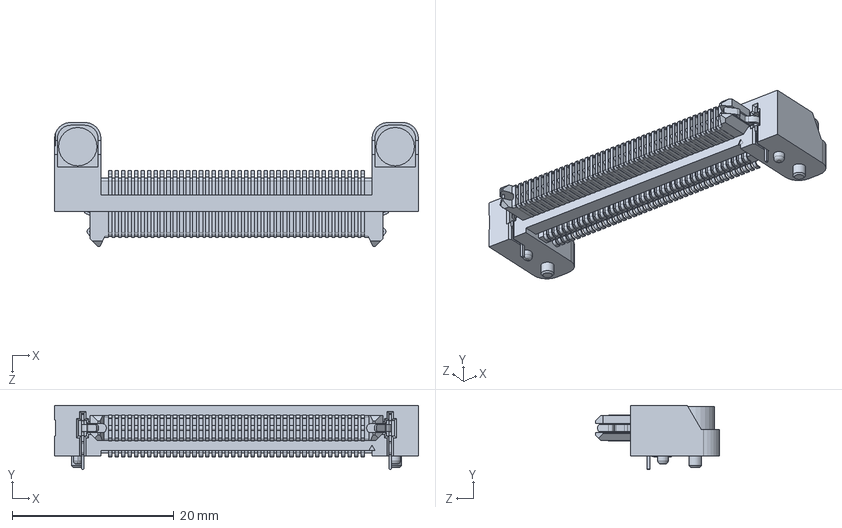
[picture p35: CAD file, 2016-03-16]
cases/NACQ Case/Assem2.SLDASM
45.0 x 7.93 x 15.4 mm
ERM8-040-01-X-D-RA-L-1
ERM8-040-01-X-D-RA-L-2

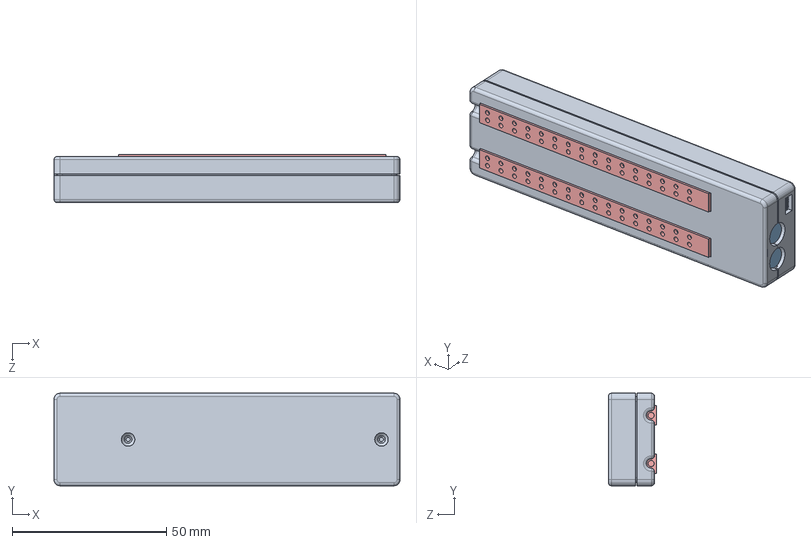
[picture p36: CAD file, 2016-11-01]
cases/Pigtail Adapter Case/two conector enclosure asm.SLDASM
112.0 x 30.0 x 15.6 mm
two conector enclosure
board
Jack PCB x 2
A79623-001
wire connector x 2

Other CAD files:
cases/Pigtail Adapter Case/J4_1.sldasm
cases/Pigtail Adapter Case/johnsboard/mill-max-0908-2-15-20-75-14-11-0_5.sldasm
cases/Pigtail Adapter Case/J2.sldasm
cases/Pigtail Adapter Case/johnsboard/J3_1.sldasm
cases/NACQ Case/ERCD-040-SBR-S-1-D_24.sldasm
cases/Pigtail Adapter Case/johnsboard/J1_1.sldasm
cases/Pigtail Adapter Case/mill-max-0908-2-15-20-75-14-11-0.sldasm
cases/Pigtail Adapter Case/johnsboard/J1_3.sldasm
cases/Easy Board Case/A79623-001.SLDPRT
cases/Easy Board Case/Samtec-ERM8-040-01-L-D-RA.SLDPRT
cases/Easy Board Case/Top.STL
cases/Easy Board Case/Top.sldprt
cases/Easy Board Case/bottom.STL
cases/Easy Board Case/bottom.sldprt
cases/Easy Board Case/easy connector board.SLDPRT
cases/Easy Board Case/easy connector box.SLDPRT
cases/Easy Board Case/easy connector box.STL
cases/Easy Board Case/samtec female.SLDPRT
cases/Intan Headstage Case/Intan RHD2164 Case Compact/Body1.sldprt
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

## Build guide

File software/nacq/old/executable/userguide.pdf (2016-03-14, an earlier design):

# TNEL Neural Acquisition User Guide

John Hermiz
v1 10/27/15

# Changes

Verision | Date | Description
v1 | 10/27/15 | Original

This document describes the initial setup and how to use the TNEL Neural Acquistion system.

# Setup

The system consists of several components illustrated below and outlined in this bullet point this:

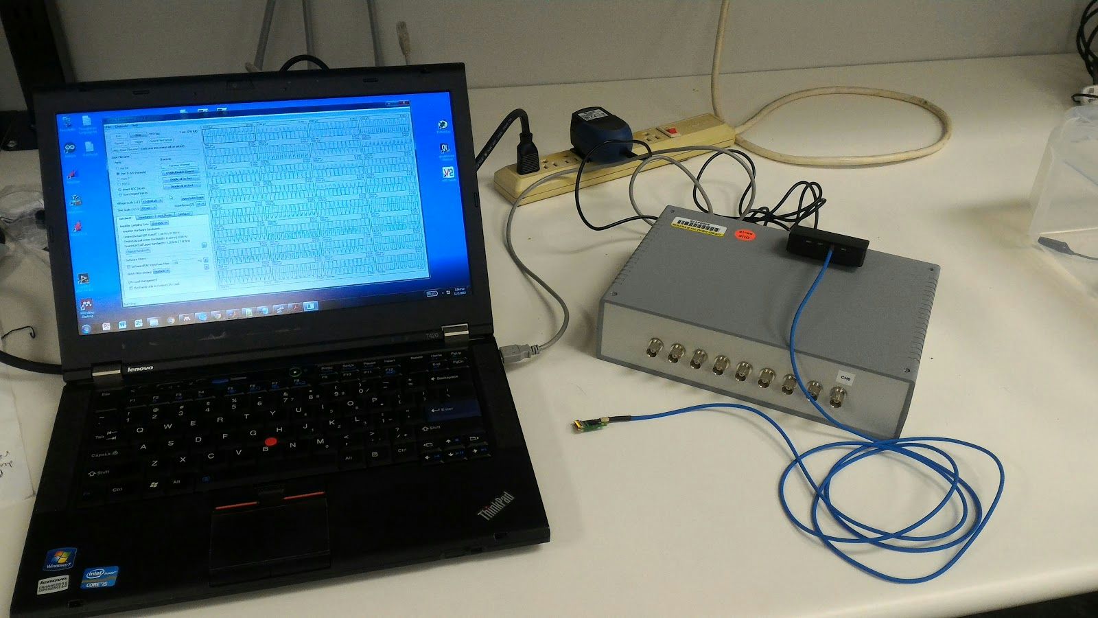
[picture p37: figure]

Entire setup including computer, neural recording box, cables and headstage chip (excludes adtech connector)

- Neural Recording Box= Receives digital data, buffers and sends to host computer via USB. Also can receive several peripheral signals (via BNC connectors), which can be used to synchronize other devices to neural acquisition.
- Adtech Connector / Headstage = Adtech connector mates with pigtails, amplifies and digitizes signal. The digital signals are send over a blue cable
- Blue Cable= This cable connects with headstage embedded in Adtech Connector and Easy Board. It is 6 ft long and transmits digital data
- Easy Connector = Adapter that mates Blue Cable with a unifying cable that feeds into the Neural Recording Box
- Power Cable= Powers Neural Recording box.
- USB Cable= Connects to Neural Recording box and computer
- Computer = Stream data to
- Battery Pack= Power Neural Recording box

# Setup

## Hardware

Connect all hardware components as shown in the above picture. Then connect USB cable to Neural Recording box and computer.

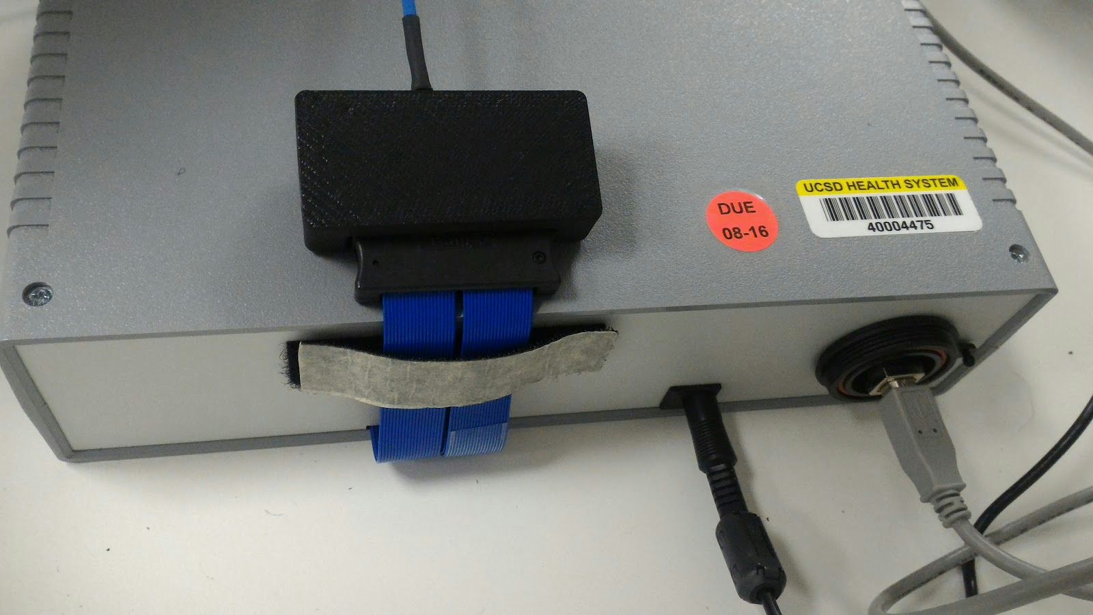
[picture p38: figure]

Connect power and usb cables into the side panel. Plug in the blue cable into the black “Easy Connector” (this can be a little tricky and the pin on the cable are quite small)

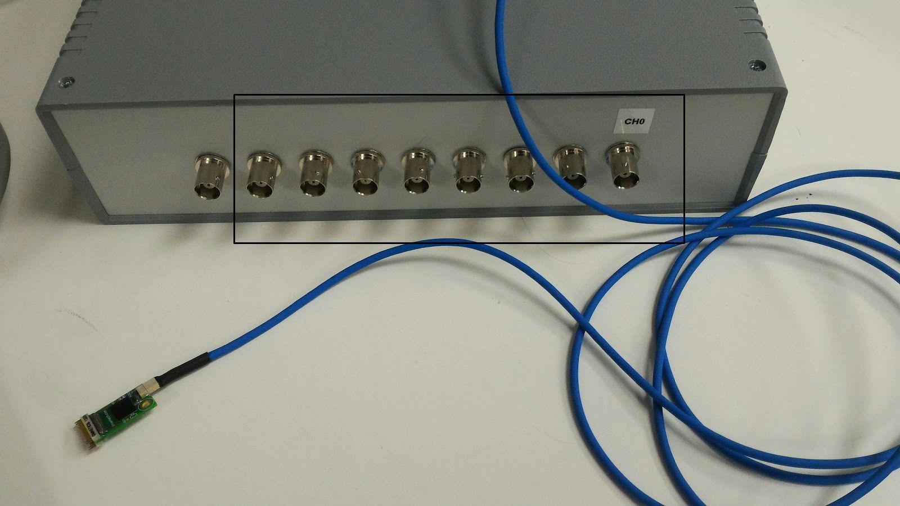
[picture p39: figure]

Connect the other end of the cable to the headstage chip. In your case, the headstage chip will be embedded into the adtech connectors. The other side panel of the neural recording box are analog inputs enclosed in the black rectangle. These inputs accept voltage between 0-3.3 V it’s very important not to exceed this range so as not to damage the electronics. You can visualize the signal feed into it with the software. Please do not connect anything to the left most input.

## Software

Note: Software has been tested on Windows 7 / 8 / 8.1 only

1. Install drivers on computer: link (http://intantech.com/files/RHD2000_USB_interface_board_drivers.zip)
2. Restart computer
3. Download Deployment folder
4. Find “RHD2000interface.exe”, right click, click “Sendto”, then click “Desktop create shortcut”
5. Double check that hardware is connected properly
6. Click “RHD2000interface.exe” shortcut to run software
7. The software should detect the headstage and should look like the picture below

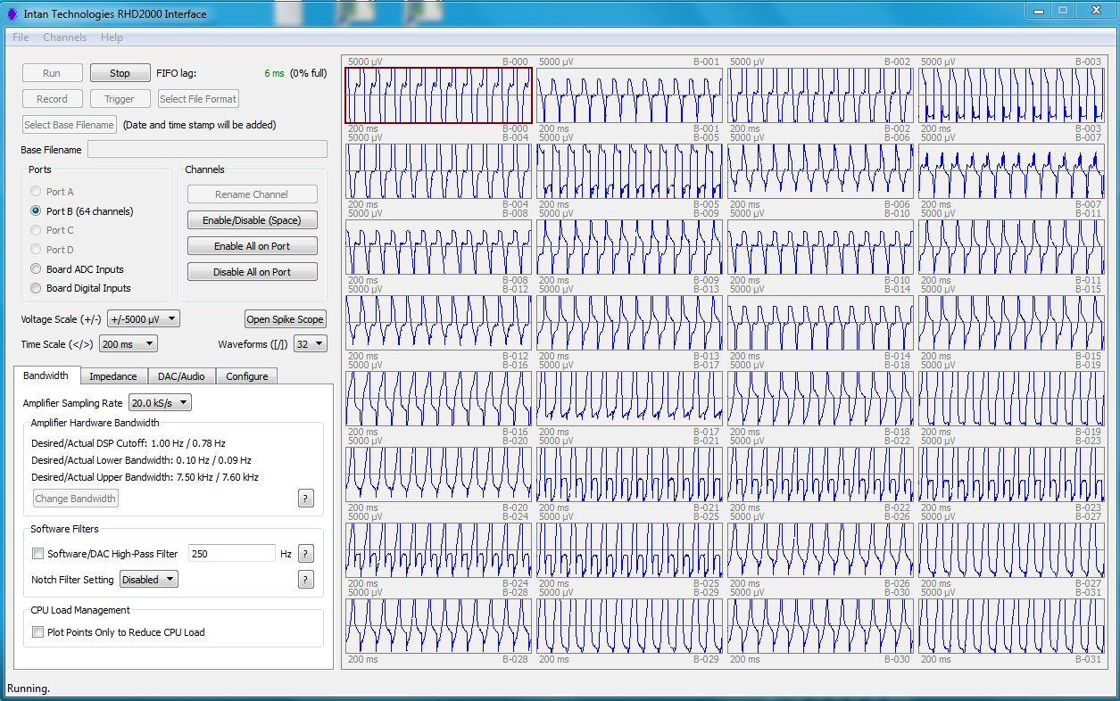
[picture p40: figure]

After installing the software and running it, the application should look similar to this. Ignore the actual waveforms shown in this picture. Familiarize yourself with the software by clicking various options and go through the various tabs.

# User Guide

## Hardware

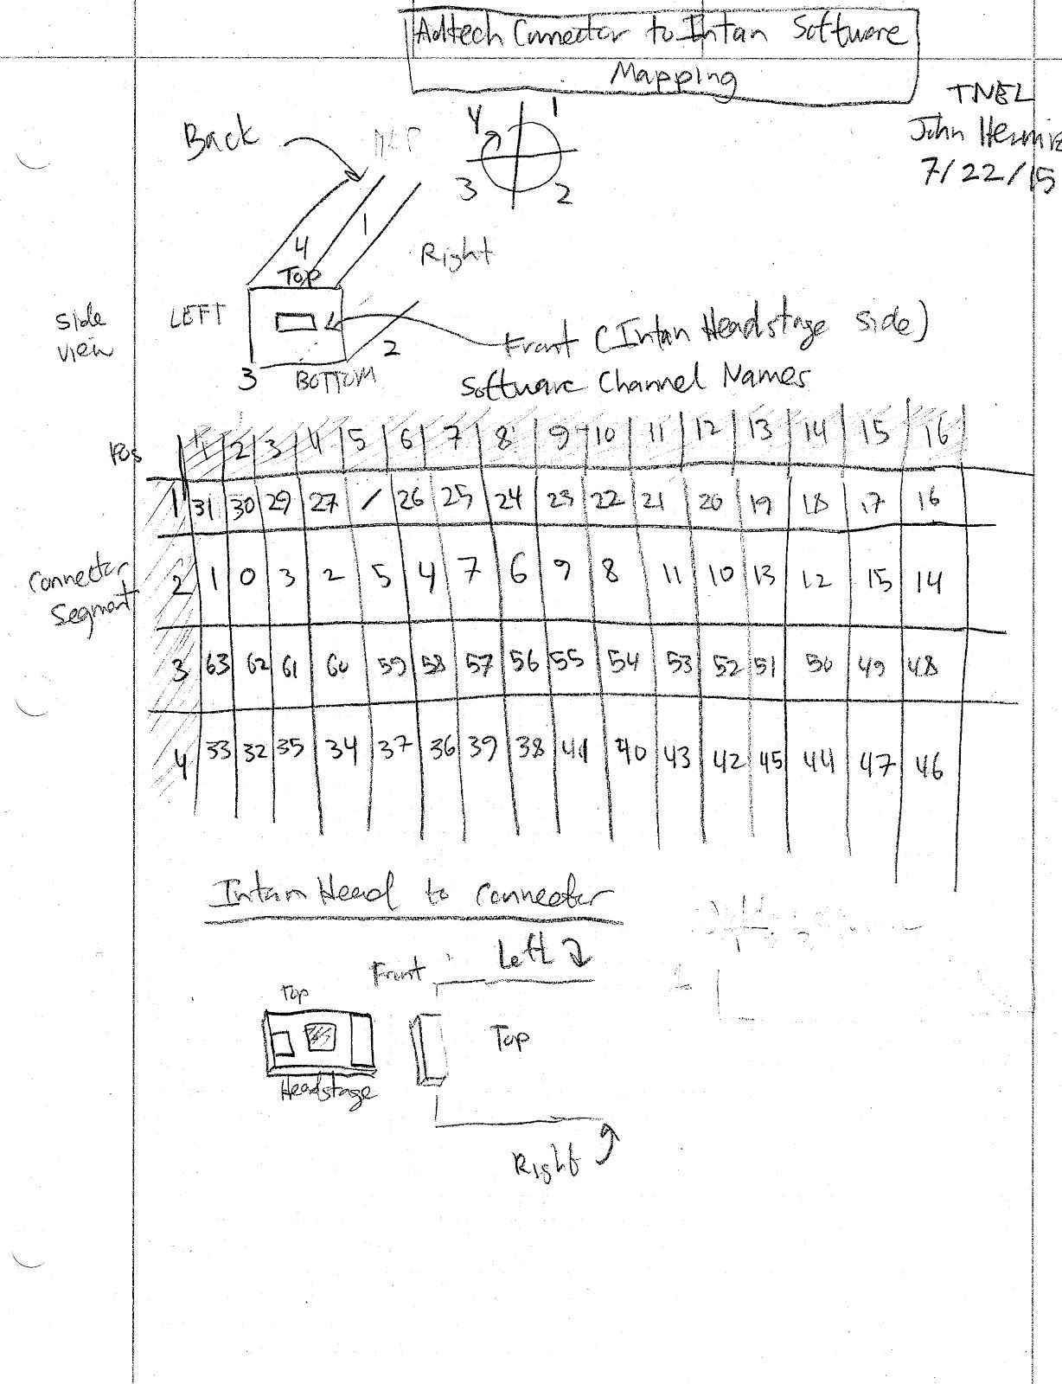
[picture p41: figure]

Get a photo of the adtech connector and write map to a table

## Software

After starting the software you should first rescan ports, indicated in the below picture

### Rescan Ports

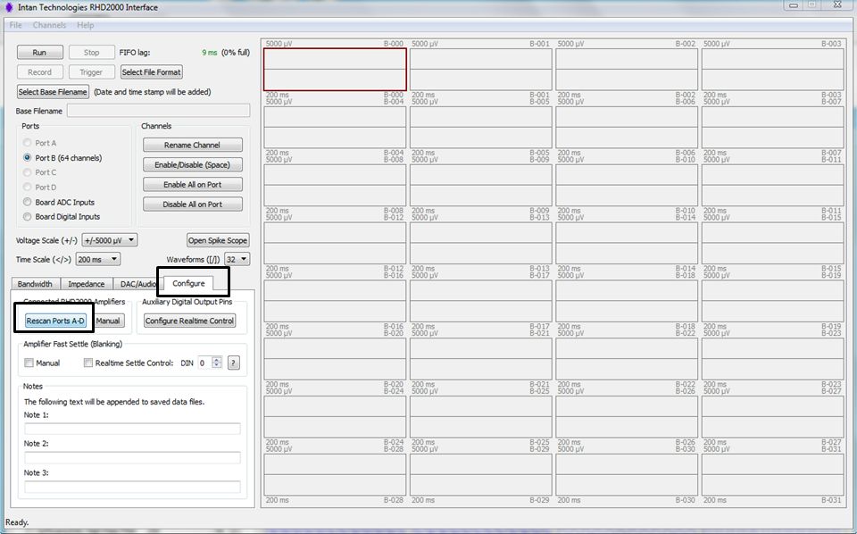
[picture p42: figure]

Go to the “Configure” tab, then click “Rescan Ports A-D” after starting application

### Impedance Test

Running an impedance test will also you to test if your electrodes are working and making good contact. Although impedances will vary greatly for different electrodes, lower impedances magnitudes are better than higher one. The impedance magnitude have units of Ω (ohms) and are displayed below the recording waveform. Also reported are the impedance phase, which has used of degrees. Almost all electrodes have an impedance phase between 0 (more like a resistor) and 90 degrees (more like a capacitor). You can save the impedance results to a commaseparatedvalue file by clicking “Save Impedance Measurement in CSV format” in the “Impedance” tab

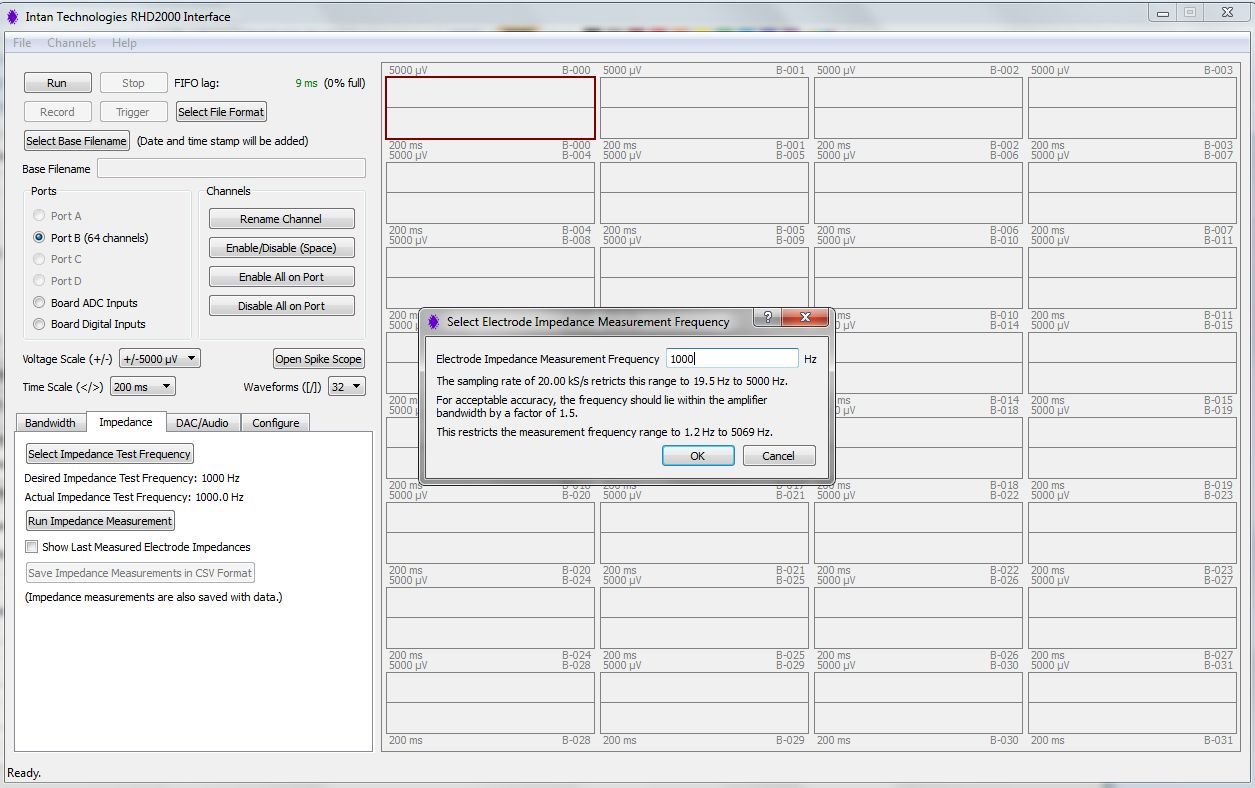
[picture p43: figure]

To run the impedance test, go to the “Impedance” tab, choose the frequency at which you would like to run the test at by clicking “Select Impedance Test Frequency”. The default value is 1000 Hz and this is generally used as a figure of merit for report impedance measurements. To actually run it, click “Run Impedance Measurement” and wait for it to complete.

### Analog Inputs

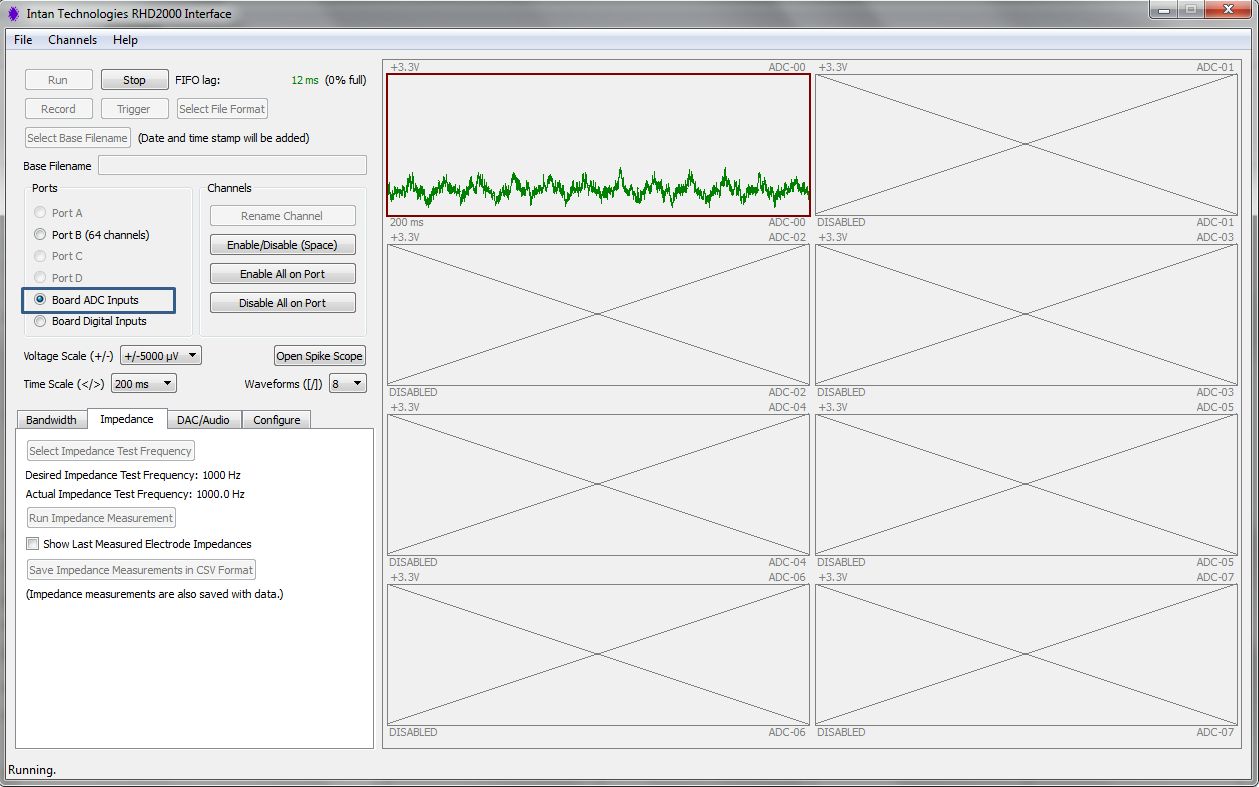
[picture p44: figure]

To visualize the analog inputs, click the “Board ADC Inputs” radio button, highlighted by the rectangle.

### Disabling Channels

When you are not taking advantages of all recording channels, it is advantageous to disable them when recording data to reduce the file size being recorded. The easiest way to disable recording channels is to click them, then press the space bar. Below is an illustration of a subset of recording channels that are disabled.

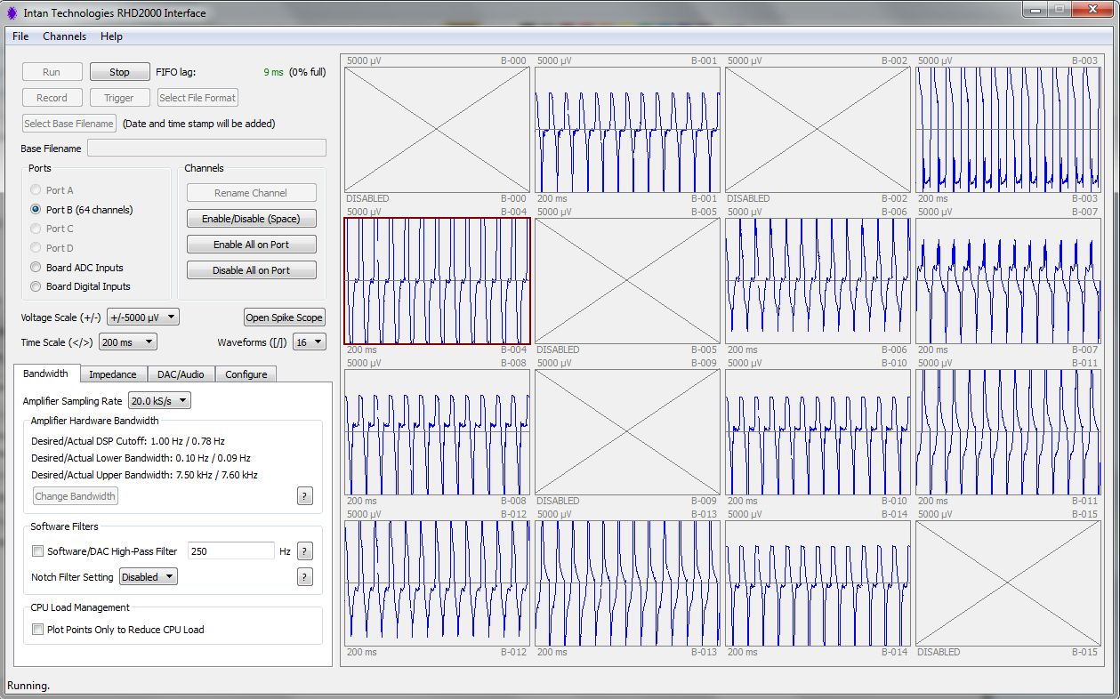
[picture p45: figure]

The channels with the ‘x’ over them are disabled. In this view, 16 channels are displayed for recording. You can display 1, 2, 4, 8, 16, and 32 waveforms simultaneous with this software. It’s important to note that channels NOT displayed are STILL being recorded.

### Detailed Software Documentation

This software is opensource and is based on software provided by Intan Technologies. Detailed user documentation can be found at the below link at pages 11-22.

http://intantech.com/files/Intan_RHD2000_eval_system.pdf

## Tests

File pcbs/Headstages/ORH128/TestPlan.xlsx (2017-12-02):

Test Plan
Does LED work?
Does the software detect the chip?
Ref shorted to ground
Ref floating
Does referencing switch work?
Does external channel switching work?

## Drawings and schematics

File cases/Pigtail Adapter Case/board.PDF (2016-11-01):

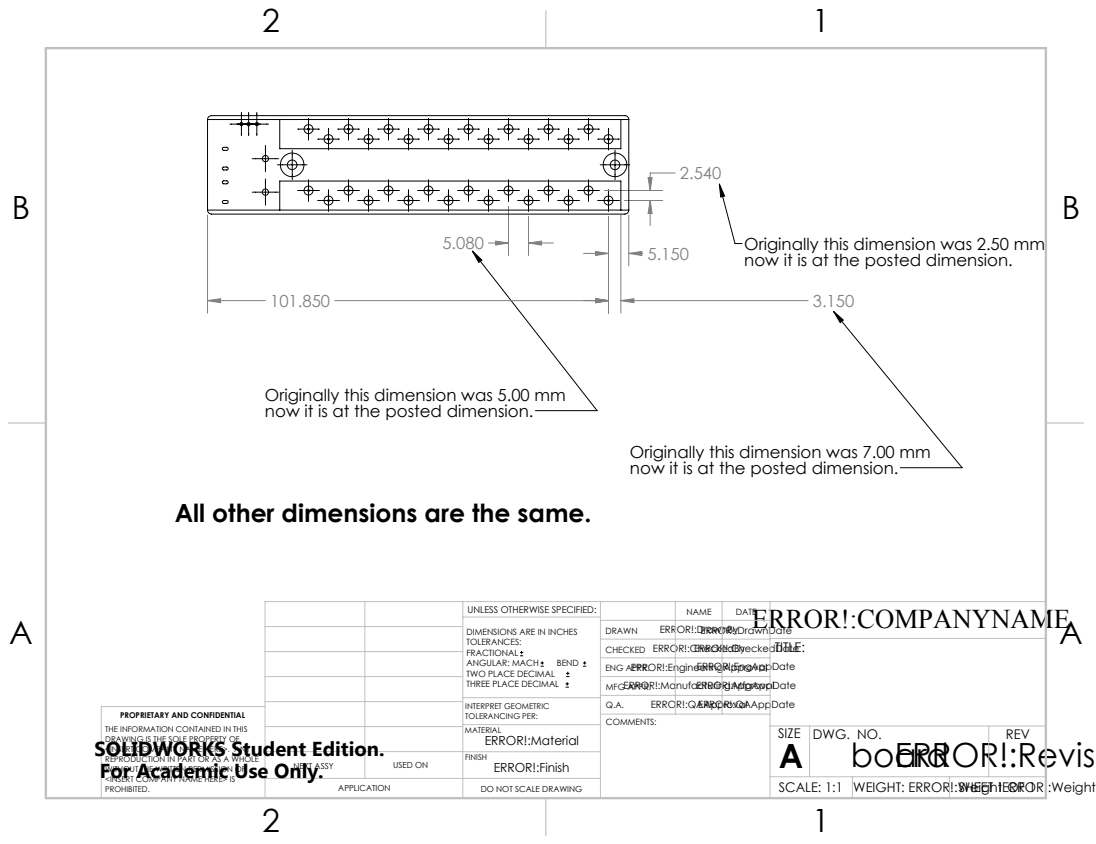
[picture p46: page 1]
SCALE: 1:1; WEIGHT: ERROR!:WeightERROR!:Weight

Originally this dimension was 2.50 mm
now it is at the posted dimension.

Originally this dimension was 5.00 mm

Originally this dimension was 7.00 mm

All other dimensions are the same.

UNLESS OTHERWISE SPECIFIED: | | | DATE ERROR!:COMPANYNAME NAME
DIMENSIONS ARE IN INCHES TOLERANCES: FRACTIONAL ANGULAR: MACH BEND TWO PLACE DECIMAL THREE PLACE DECIMAL | DRAWN ERROR!:DrawnBy | ERROR!:DrawnDate

ERROR!:CheckedBy CHECKED | ERROR!:CheckedDate | | TITLE:
ENG APPR. ERROR!:EngineeringApproval | ERROR!:EngAppDate
ERROR!:ManufacturingApproval MFG APPR. | ERROR!:MfgAppDate

INTERPRET GEOMETRIC TOLERANCING PER: | Q.A. ERROR!:QAApproval ERROR!:QAAppDate
MATERIAL | | SIZE A | DWG. NO. board | REV

PROPRIETARY AND CONFIDENTIAL
THE INFORMATION CONTAINED IN THIS
DRAWING IS THE SOLE PROPERTY OF
SOLIDWORKS Student Edition.
<INSERT COMPANY NAME HERE>. ANY
REPRODUCTION IN PART OR AS A WHOLE
For Academic Use Only.
WITHOUT THE WRITTEN PERMISSION OF
<INSERT COMPANY NAME HERE> IS
PROHIBITED.

NEXT ASSY | USED ON | ERROR!:Finish FINISH

APPLICATION | DO NOT SCALE DRAWING | | | | SHEET 1 OF 1

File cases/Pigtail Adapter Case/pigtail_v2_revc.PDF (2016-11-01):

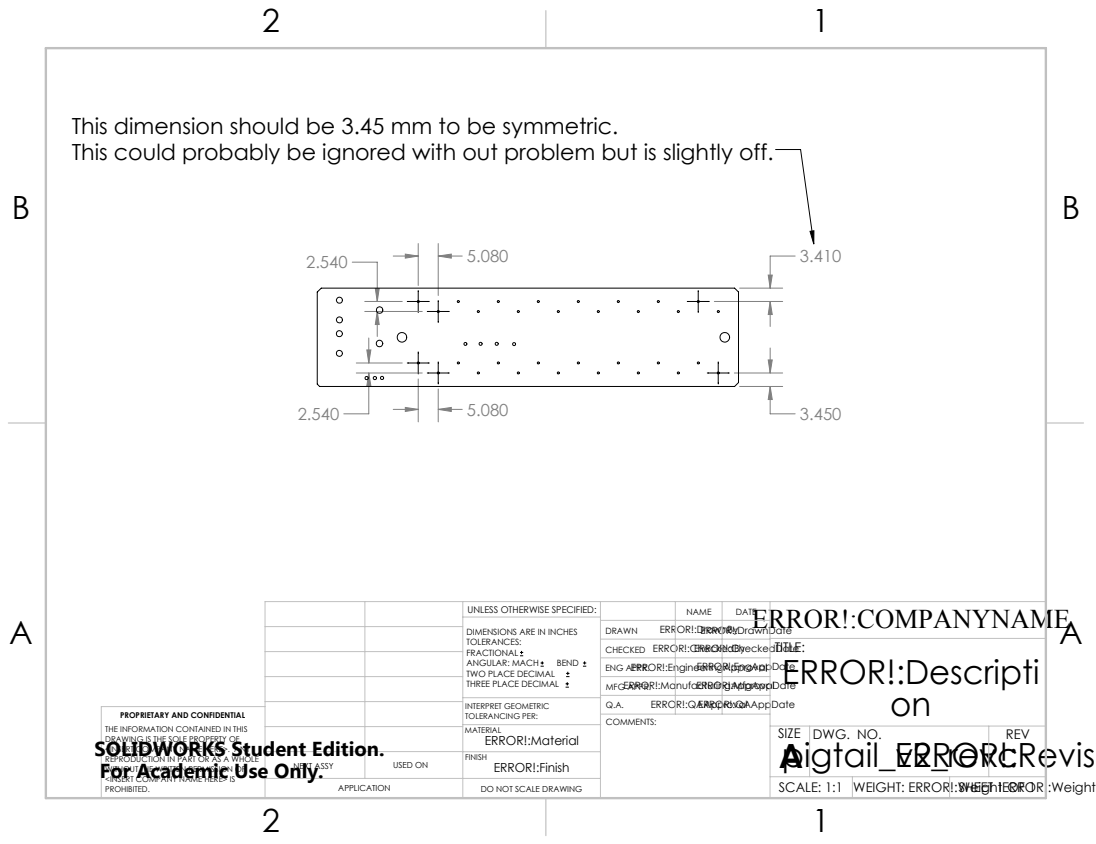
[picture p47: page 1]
SCALE: 1:1; WEIGHT: ERROR!:WeightERROR!:Weight

This dimension should be 3.45 mm to be symmetric.
This could probably be ignored with out problem but is slightly off.

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

ERROR!:CheckedBy CHECKED | ERROR!:CheckedDate | | TITLE: ERROR!:Descripti on
ENG APPR. ERROR!:EngineeringApproval | ERROR!:EngAppDate
ERROR!:ManufacturingApproval MFG APPR. | ERROR!:MfgAppDate

INTERPRET GEOMETRIC TOLERANCING PER: | Q.A. ERROR!:QAApproval ERROR!:QAAppDate
MATERIAL ERROR!:Material | | SIZE A pigtail_v2_revc | DWG. NO. | REV

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

NEXT ASSY | USED ON | ERROR!:Finish FINISH

APPLICATION | DO NOT SCALE DRAWING | | | | SHEET 1 OF 1

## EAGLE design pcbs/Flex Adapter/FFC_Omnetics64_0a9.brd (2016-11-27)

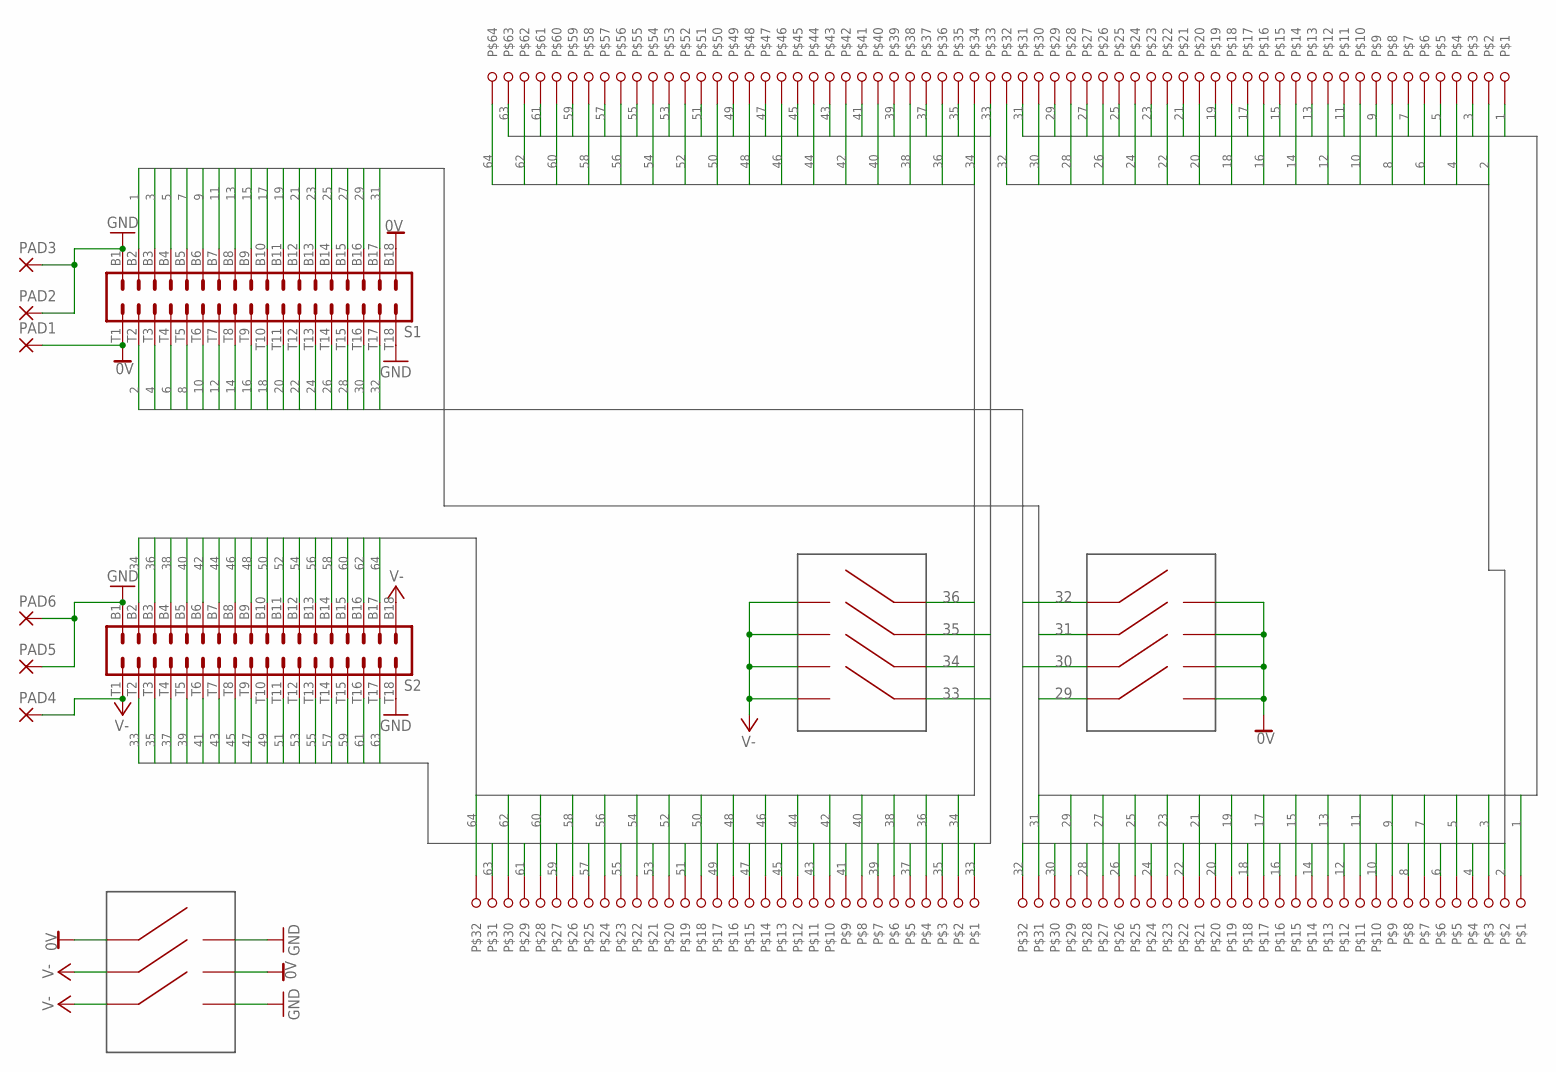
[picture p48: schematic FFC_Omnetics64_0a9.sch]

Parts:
PAD1, PAD2, PAD3, PAD4, PAD5, PAD6: 2,15/1,0
S1, S2: OMNETICS_A79024
U$1: OMRON64FFC-0.5MM; OMRONFFC64-0.5MM
U$2, U$3: OMRON32FFC-0.5MM; OMRON32
U$4, U$5: DIPSWITCH-4POS
U$6: DIPSWITCH-3POS

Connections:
0V: PAD1.1, S1.B18, S1.T1, U$4.P$5, U$4.P$6, U$4.P$7, U$4.P$8, U$6.P$1, U$6.P$5
1: S1.B2, U$1.P$64, U$3.P$32
2: S1.T2, U$1.P$63, U$3.P$31
3: S1.B3, U$1.P$62, U$3.P$30
4: S1.T3, U$1.P$61, U$3.P$29
5: S1.B4, U$1.P$60, U$3.P$28
6: S1.T4, U$1.P$59, U$3.P$27
7: S1.B5, U$1.P$58, U$3.P$26
8: S1.T5, U$1.P$57, U$3.P$25
9: S1.B6, U$1.P$56, U$3.P$24
10: S1.T6, U$1.P$55, U$3.P$23
11: S1.B7, U$1.P$54, U$3.P$22
12: S1.T7, U$1.P$53, U$3.P$21
13: S1.B8, U$1.P$52, U$3.P$20
14: S1.T8, U$1.P$51, U$3.P$19
15: S1.B9, U$1.P$50, U$3.P$18
16: S1.T9, U$1.P$49, U$3.P$17
17: S1.B10, U$1.P$48, U$3.P$16
18: S1.T10, U$1.P$47, U$3.P$15
19: S1.B11, U$1.P$46, U$3.P$14
20: S1.T11, U$1.P$45, U$3.P$13
21: S1.B12, U$1.P$44, U$3.P$12
22: S1.T12, U$1.P$43, U$3.P$11
23: S1.B13, U$1.P$42, U$3.P$10
24: S1.T13, U$1.P$41, U$3.P$9
25: S1.B14, U$1.P$40, U$3.P$8
26: S1.T14, U$1.P$39, U$3.P$7
27: S1.B15, U$1.P$38, U$3.P$6
28: S1.T15, U$1.P$37, U$3.P$5
29: S1.B16, U$1.P$36, U$3.P$4, U$4.P$4
30: S1.T16, U$1.P$35, U$3.P$3, U$4.P$3
31: S1.B17, U$1.P$34, U$3.P$2, U$4.P$2
32: S1.T17, U$1.P$33, U$3.P$1, U$4.P$1
33: S2.T2, U$1.P$32, U$2.P$32, U$5.P$4
34: S2.B2, U$1.P$31, U$2.P$31, U$5.P$3
35: S2.T3, U$1.P$30, U$2.P$30, U$5.P$2
36: S2.B3, U$1.P$29, U$2.P$29, U$5.P$1
37: S2.T4, U$1.P$28, U$2.P$28
38: S2.B4, U$1.P$27, U$2.P$27
39: S2.T5, U$1.P$26, U$2.P$26
40: S2.B5, U$1.P$25, U$2.P$25
41: S2.T6, U$1.P$24, U$2.P$24
42: S2.B6, U$1.P$23, U$2.P$23
43: S2.T7, U$1.P$22, U$2.P$22
44: S2.B7, U$1.P$21, U$2.P$21
45: S2.T8, U$1.P$20, U$2.P$20
46: S2.B8, U$1.P$19, U$2.P$19
47: S2.T9, U$1.P$18, U$2.P$18
48: S2.B9, U$1.P$17, U$2.P$17
49: S2.T10, U$1.P$16, U$2.P$16
50: S2.B10, U$1.P$15, U$2.P$15
51: S2.T11, U$1.P$14, U$2.P$14
52: S2.B11, U$1.P$13, U$2.P$13
53: S2.T12, U$1.P$12, U$2.P$12
54: S2.B12, U$1.P$11, U$2.P$11
55: S2.T13, U$1.P$10, U$2.P$10
56: S2.B13, U$1.P$9, U$2.P$9
57: S2.T14, U$1.P$8, U$2.P$8
58: S2.B14, U$1.P$7, U$2.P$7
59: S2.T15, U$1.P$6, U$2.P$6
60: S2.B15, U$1.P$5, U$2.P$5
61: S2.T16, U$1.P$4, U$2.P$4
62: S2.B16, U$1.P$3, U$2.P$3
63: S2.T17, U$1.P$2, U$2.P$2
64: S2.B17, U$1.P$1, U$2.P$1
GND: PAD2.1, PAD3.1, PAD5.1, PAD6.1, S1.B1, S1.T18, S2.B1, S2.T18, U$6.P$4, U$6.P$6
V-: PAD4.1, S2.B18, S2.T1, U$5.P$5, U$5.P$6, U$5.P$7, U$5.P$8, U$6.P$2, U$6.P$3

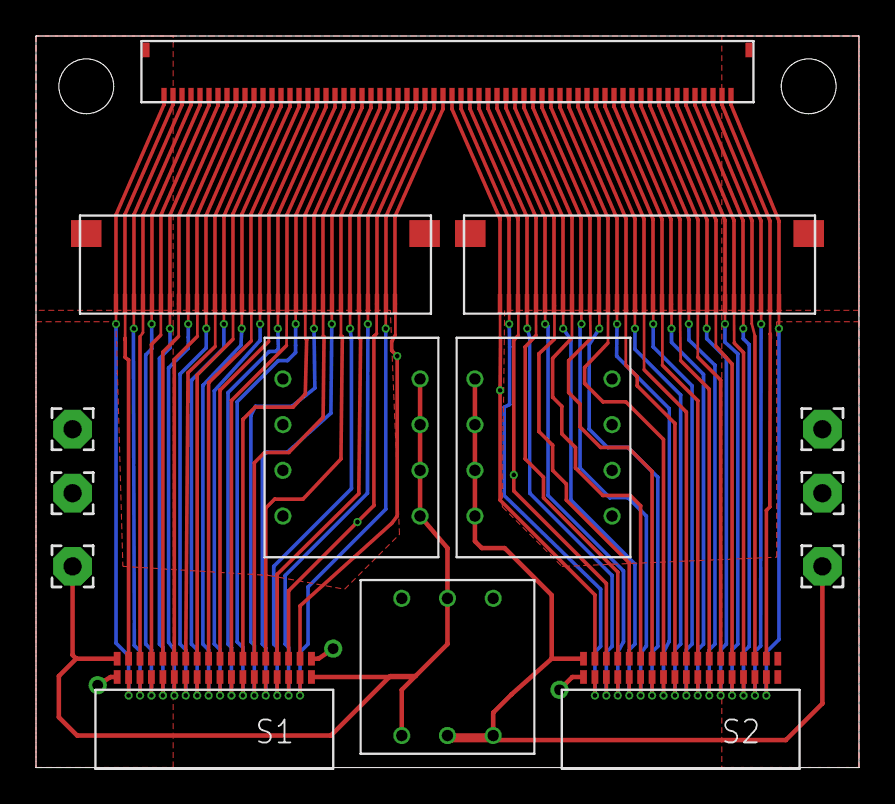
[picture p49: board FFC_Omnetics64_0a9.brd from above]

Board: 4 copper layers, 45.7 x 40.6 mm, 14 parts (0 on the bottom side), 67 nets.

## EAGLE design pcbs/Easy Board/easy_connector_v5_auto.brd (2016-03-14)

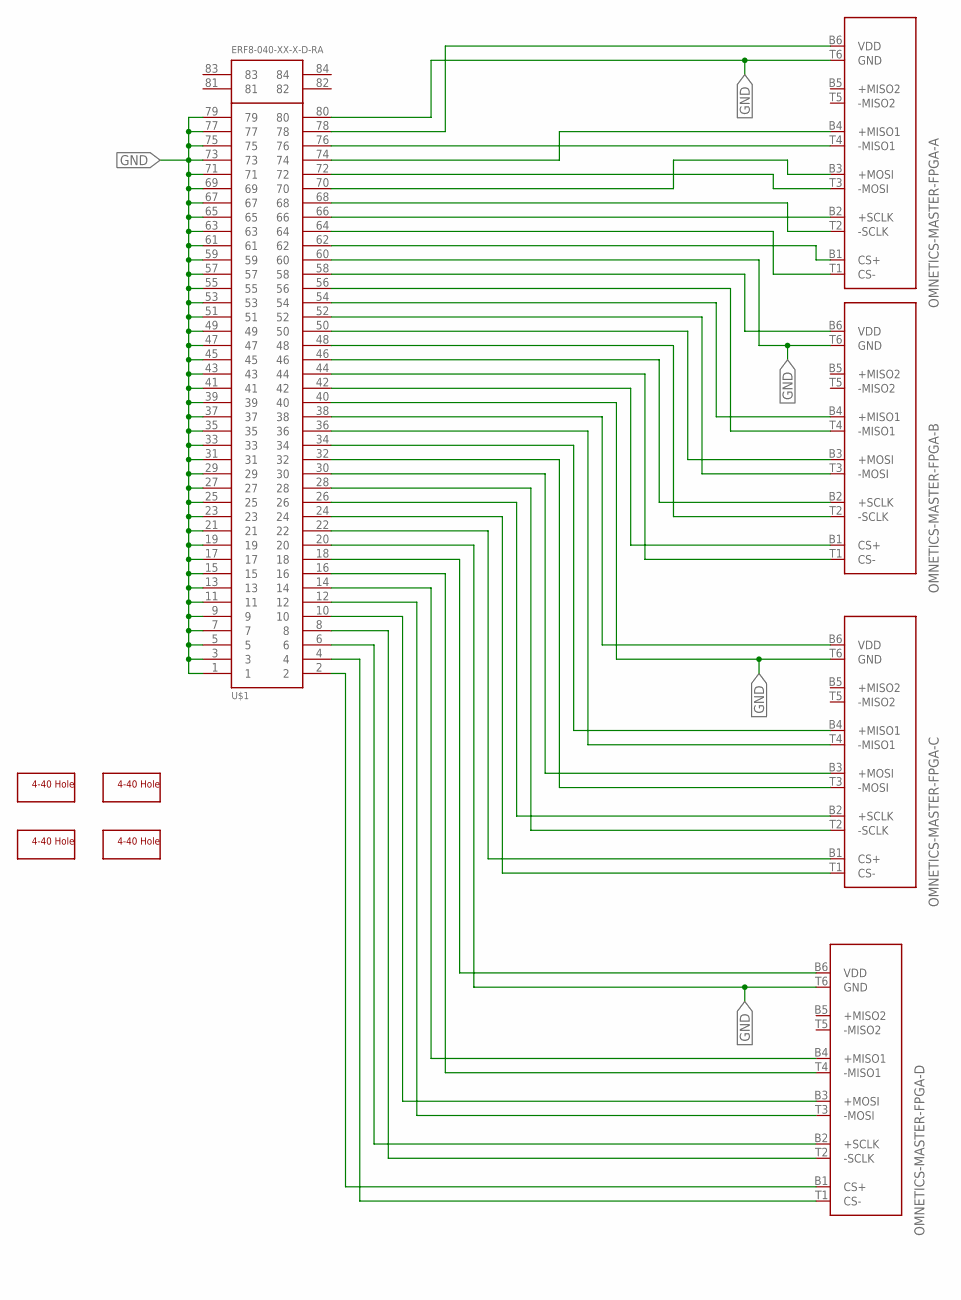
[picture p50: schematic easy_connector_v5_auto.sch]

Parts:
H1, H2, H3, H4: SCREW_HOLE_4-40
OMNETICS-MASTER-FPGA-A: OMNETIC-CONNECTOR; OMNETICS_PZN-12-AA-UPDATED
OMNETICS-MASTER-FPGA-B: OMNETIC-CONNECTOR; OMNETICS_PZN-12-AA-UPDATED
OMNETICS-MASTER-FPGA-C: OMNETIC-CONNECTOR; OMNETICS_PZN-12-AA-UPDATED
OMNETICS-MASTER-FPGA-D: OMNETIC-CONNECTOR; OMNETICS_PZN-12-AA-UPDATED
U$1: ERF8-040-XX-X-D-RA

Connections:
GND: OMNETICS-MASTER-FPGA-A.T6 (GND), OMNETICS-MASTER-FPGA-B.T6 (GND), OMNETICS-MASTER-FPGA-C.T6 (GND), OMNETICS-MASTER-FPGA-D.T6 (GND), U$1.1, U$1.3, U$1.5, U$1.7, U$1.9, U$1.11, U$1.13, U$1.15, U$1.17, U$1.19, U$1.20, U$1.21, U$1.23, U$1.25, U$1.27, U$1.29, U$1.31, U$1.33, U$1.35, U$1.37, U$1.39, U$1.40, U$1.41, U$1.43, U$1.45, U$1.47, U$1.49, U$1.51, U$1.53, U$1.55, U$1.57, U$1.59, U$1.60, U$1.61, U$1.63, U$1.65, U$1.67, U$1.69, U$1.71, U$1.73, U$1.75, U$1.77, U$1.79, U$1.80
MISO1_N: OMNETICS-MASTER-FPGA-A.T4 (-MISO1), U$1.76
MISO1_P: OMNETICS-MASTER-FPGA-A.B4 (+MISO1), U$1.74
unnamed: OMNETICS-MASTER-FPGA-A.T3 (-MOSI), U$1.72
unnamed: OMNETICS-MASTER-FPGA-A.B3 (+MOSI), U$1.70
unnamed: OMNETICS-MASTER-FPGA-A.T2 (-SCLK), U$1.68
unnamed: OMNETICS-MASTER-FPGA-A.B2 (+SCLK), U$1.66
unnamed: OMNETICS-MASTER-FPGA-A.T1 (CS-), U$1.64
unnamed: OMNETICS-MASTER-FPGA-A.B1 (CS+), U$1.62
unnamed: OMNETICS-MASTER-FPGA-B.T4 (-MISO1), U$1.56
unnamed: OMNETICS-MASTER-FPGA-B.B4 (+MISO1), U$1.54
unnamed: OMNETICS-MASTER-FPGA-B.T3 (-MOSI), U$1.52
unnamed: OMNETICS-MASTER-FPGA-B.B3 (+MOSI), U$1.50
unnamed: OMNETICS-MASTER-FPGA-B.T2 (-SCLK), U$1.48
unnamed: OMNETICS-MASTER-FPGA-B.B2 (+SCLK), U$1.46
unnamed: OMNETICS-MASTER-FPGA-B.T1 (CS-), U$1.44
unnamed: OMNETICS-MASTER-FPGA-B.B1 (CS+), U$1.42
unnamed: OMNETICS-MASTER-FPGA-C.T4 (-MISO1), U$1.36
unnamed: OMNETICS-MASTER-FPGA-C.B4 (+MISO1), U$1.34
unnamed: OMNETICS-MASTER-FPGA-C.T3 (-MOSI), U$1.32
unnamed: OMNETICS-MASTER-FPGA-C.B3 (+MOSI), U$1.30
unnamed: OMNETICS-MASTER-FPGA-C.T2 (-SCLK), U$1.28
unnamed: OMNETICS-MASTER-FPGA-C.B2 (+SCLK), U$1.26
unnamed: OMNETICS-MASTER-FPGA-C.T1 (CS-), U$1.24
unnamed: OMNETICS-MASTER-FPGA-C.B1 (CS+), U$1.22
unnamed: OMNETICS-MASTER-FPGA-D.T4 (-MISO1), U$1.16
unnamed: OMNETICS-MASTER-FPGA-D.B4 (+MISO1), U$1.14
unnamed: OMNETICS-MASTER-FPGA-D.T3 (-MOSI), U$1.12
unnamed: OMNETICS-MASTER-FPGA-D.B3 (+MOSI), U$1.10
unnamed: OMNETICS-MASTER-FPGA-D.T2 (-SCLK), U$1.8
unnamed: OMNETICS-MASTER-FPGA-D.B2 (+SCLK), U$1.6
unnamed: OMNETICS-MASTER-FPGA-D.T1 (CS-), U$1.4
unnamed: OMNETICS-MASTER-FPGA-D.B1 (CS+), U$1.2
VDD-A: OMNETICS-MASTER-FPGA-A.B6 (VDD), U$1.78
VDD-B: OMNETICS-MASTER-FPGA-B.B6 (VDD), U$1.58
VDD-C: OMNETICS-MASTER-FPGA-C.B6 (VDD), U$1.38
VDD-D: OMNETICS-MASTER-FPGA-D.B6 (VDD), U$1.18

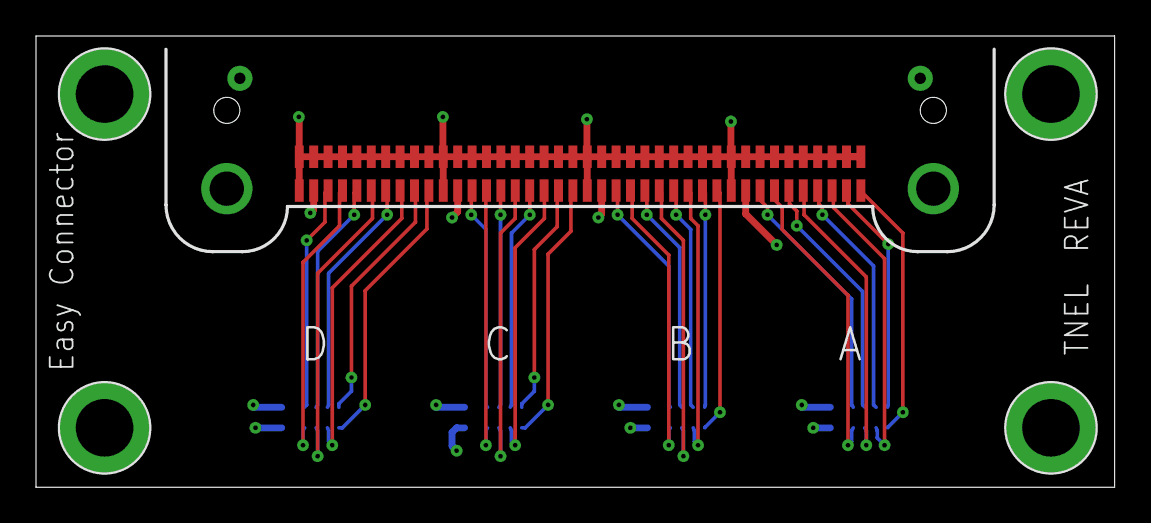
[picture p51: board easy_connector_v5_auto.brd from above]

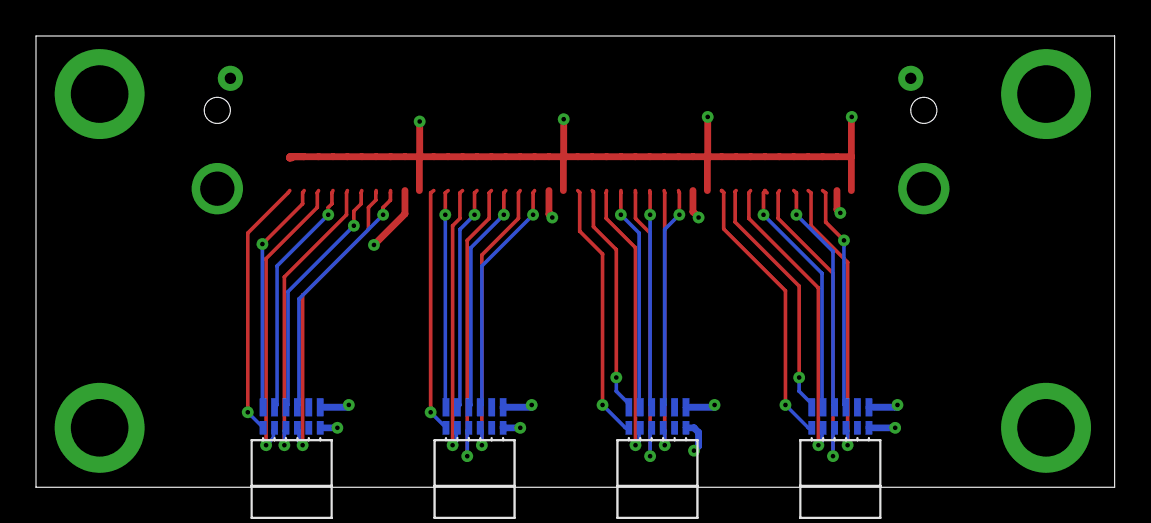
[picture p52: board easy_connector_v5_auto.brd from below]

Board: 4 copper layers, 59.9 x 25.1 mm, 9 parts (4 on the bottom side), 37 nets.

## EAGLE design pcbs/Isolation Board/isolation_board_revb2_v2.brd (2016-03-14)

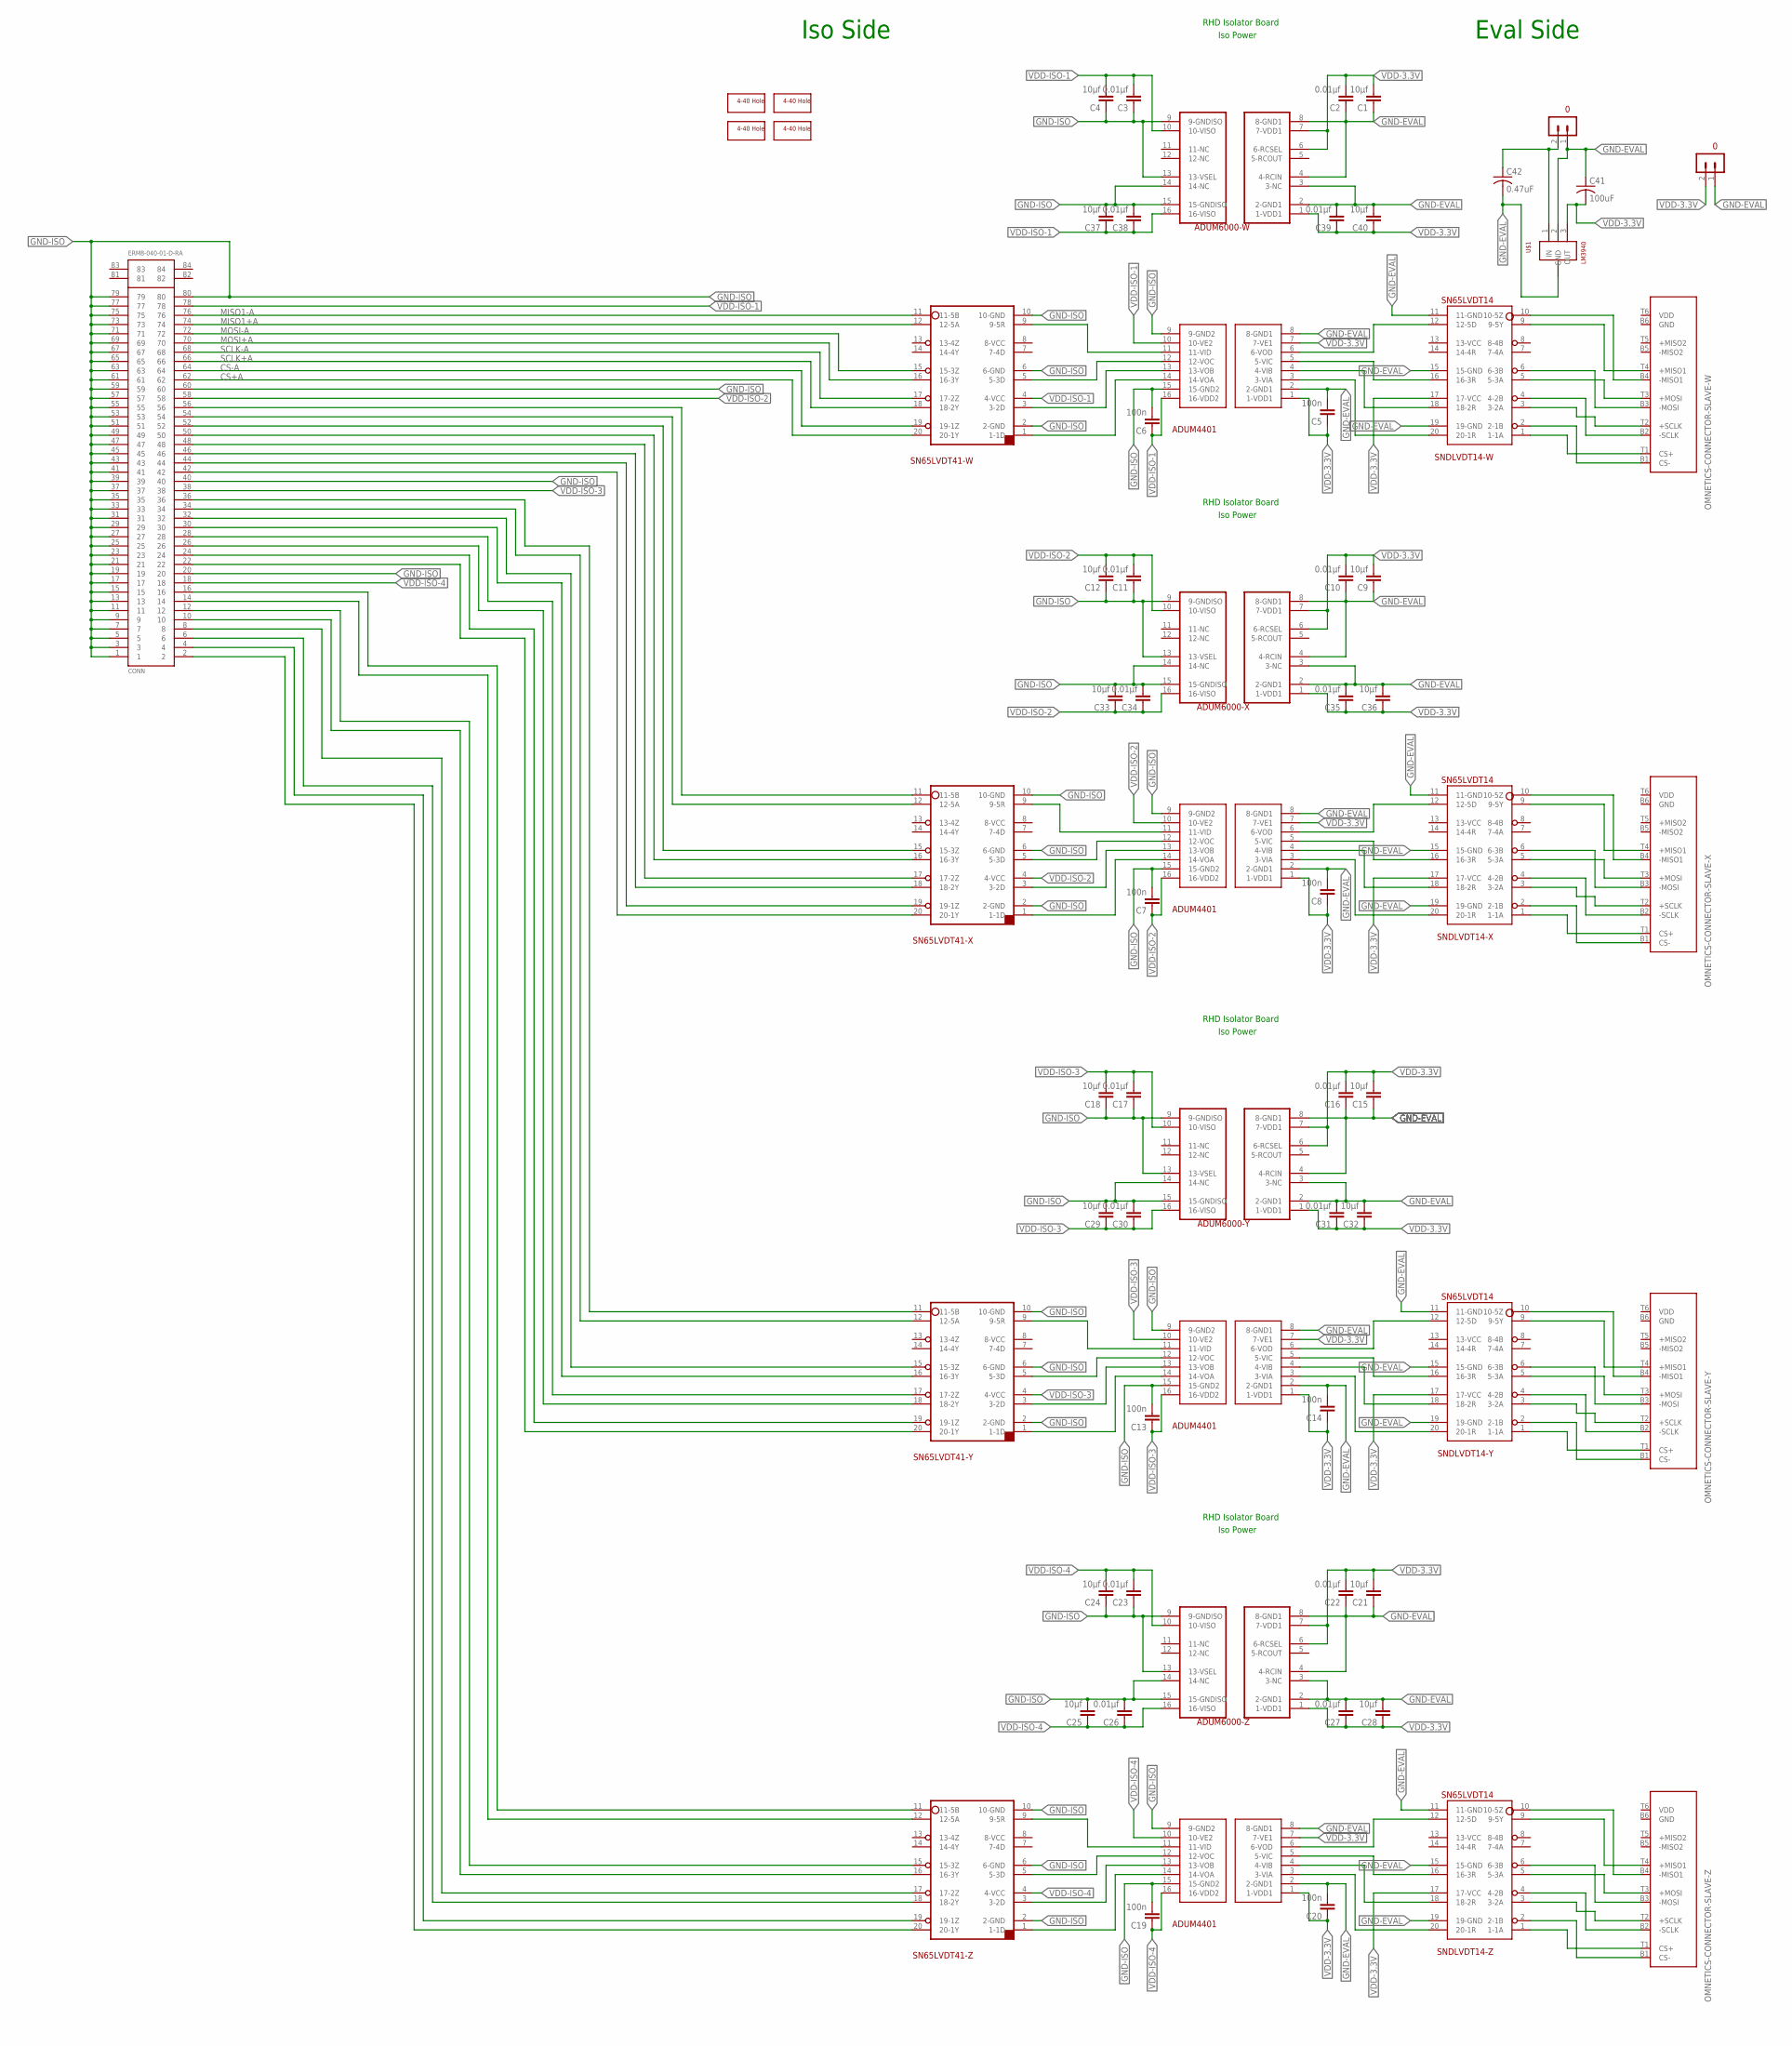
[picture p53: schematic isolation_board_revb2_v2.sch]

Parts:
ADUM4401-W, ADUM4401-X, ADUM4401-Y, ADUM4401-Z: ADUM4401; SOIC16R
ADUM6000-W, ADUM6000-X, ADUM6000-Y, ADUM6000-Z: ADUM6000; SOIC16R; MPN ADUM6000ARWZ
C1, C4, C9, C12, C15, C18, C21, C24, C25, C28, C29, C32, C33, C36, C37, C40: 10µf; 0805
C2, C3, C10, C11, C16, C17, C22, C23, C26, C27, C30, C31, C34, C35, C38, C39: 0.01µf; 0805
C5, C6, C7, C8, C13, C14, C19, C20: 100n; 0805
C41: 100uF; C1206
C42: 0.47uF; C0603
CONN: ERM8-040-01-D-RA
H1, H2, H3, H4: SCREW_HOLE_4-40
OMNETICS-CONNECTOR-SLAVE-W: OMNETICS-CONNECTOR-SLAVE-SIDE; OMNETICS_PZN-12-AA-UPDATED
OMNETICS-CONNECTOR-SLAVE-X: OMNETICS-CONNECTOR-SLAVE-SIDE; OMNETICS_PZN-12-AA-UPDATED
OMNETICS-CONNECTOR-SLAVE-Y: OMNETICS-CONNECTOR-SLAVE-SIDE; OMNETICS_PZN-12-AA-UPDATED
OMNETICS-CONNECTOR-SLAVE-Z: OMNETICS-CONNECTOR-SLAVE-SIDE; OMNETICS_PZN-12-AA-UPDATED
S1: TERMINAL_BLOCK_2-3.5MM-5V; TERMINAL_BLOCK_3.5MM_2_5V
S2: TERMINAL_BLOCK_2-3.5MM-3.3V; TERMINAL_BLOCK_3.5MM_2_3.3V
SN65LVDT41-W, SN65LVDT41-X, SN65LVDT41-Y, SN65LVDT41-Z: SN65LVDT41; SN65LVDT41-UPDATED
SNDLVDT14-W, SNDLVDT14-X, SNDLVDT14-Y, SNDLVDT14-Z: SN65LVDT14; SN65LDVT14
U$1: LM3940; SOT223

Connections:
CS+A: CONN.62, SN65LVDT41-W.20 (20-1Y)
CS-A: CONN.64, SN65LVDT41-W.19 (19-1Z)
GND-EVAL: ADUM4401-W.2 (2-GND1), ADUM4401-W.8 (8-GND1), ADUM4401-X.2 (2-GND1), ADUM4401-X.8 (8-GND1), ADUM4401-Y.2 (2-GND1), ADUM4401-Y.8 (8-GND1), ADUM4401-Z.2 (2-GND1), ADUM4401-Z.8 (8-GND1), ADUM6000-W.2 (2-GND1), ADUM6000-W.3 (3-NC), ADUM6000-W.4 (4-RCIN), ADUM6000-W.8 (8-GND1), ADUM6000-X.2 (2-GND1), ADUM6000-X.3 (3-NC), ADUM6000-X.4 (4-RCIN), ADUM6000-X.8 (8-GND1), ADUM6000-Y.2 (2-GND1), ADUM6000-Y.3 (3-NC), ADUM6000-Y.4 (4-RCIN), ADUM6000-Y.8 (8-GND1), ADUM6000-Z.2 (2-GND1), ADUM6000-Z.3 (3-NC), ADUM6000-Z.4 (4-RCIN), ADUM6000-Z.8 (8-GND1), C1.1, C2.1, C5.2, C8.2, C9.1, C10.1, C14.2, C15.1, C16.1, C20.2, C21.1, C22.1, C27.2, C28.2, C31.2, C32.2, C35.2, C36.2, C39.2, C40.2, C41.1, C42.2, S1.1 (0), S2.1 (0), SNDLVDT14-W.11 (11-GND), SNDLVDT14-W.15 (15-GND), SNDLVDT14-W.19 (19-GND), SNDLVDT14-X.11 (11-GND), SNDLVDT14-X.15 (15-GND), SNDLVDT14-X.19 (19-GND), SNDLVDT14-Y.11 (11-GND), SNDLVDT14-Y.15 (15-GND), SNDLVDT14-Y.19 (19-GND), SNDLVDT14-Z.11 (11-GND), SNDLVDT14-Z.15 (15-GND), SNDLVDT14-Z.19 (19-GND), U$1.2 (GND), U$1.4 (GND_T)
GND-ISO: ADUM4401-W.9 (9-GND2), ADUM4401-W.15 (15-GND2), ADUM4401-X.9 (9-GND2), ADUM4401-X.15 (15-GND2), ADUM4401-Y.9 (9-GND2), ADUM4401-Y.15 (15-GND2), ADUM4401-Z.9 (9-GND2), ADUM4401-Z.15 (15-GND2), ADUM6000-W.9 (9-GNDISO), ADUM6000-W.13 (13-VSEL), ADUM6000-W.14 (14-NC), ADUM6000-W.15 (15-GNDISO), ADUM6000-X.9 (9-GNDISO), ADUM6000-X.13 (13-VSEL), ADUM6000-X.14 (14-NC), ADUM6000-X.15 (15-GNDISO), ADUM6000-Y.9 (9-GNDISO), ADUM6000-Y.13 (13-VSEL), ADUM6000-Y.14 (14-NC), ADUM6000-Y.15 (15-GNDISO), ADUM6000-Z.9 (9-GNDISO), ADUM6000-Z.13 (13-VSEL), ADUM6000-Z.14 (14-NC), ADUM6000-Z.15 (15-GNDISO), C3.1, C4.1, C6.2, C7.2, C11.1, C12.1, C13.2, C17.1, C18.1, C19.2, C23.1, C24.1, C25.2, C26.2, C29.2, C30.2, C33.2, C34.2, C37.2, C38.2, CONN.1, CONN.3, CONN.5, CONN.7, CONN.9, CONN.11, CONN.13, CONN.15, CONN.17, CONN.19, CONN.20, CONN.21, CONN.23, CONN.25, CONN.27, CONN.29, CONN.31, CONN.33, CONN.35, CONN.37, CONN.39, CONN.40, CONN.41, CONN.43, CONN.45, CONN.47, CONN.49, CONN.51, CONN.53, CONN.55, CONN.57, CONN.59, CONN.60, CONN.61, CONN.63, CONN.65, CONN.67, CONN.69, CONN.71, CONN.73, CONN.75, CONN.77, CONN.79, CONN.80, SN65LVDT41-W.2 (2-GND), SN65LVDT41-W.6 (6-GND), SN65LVDT41-W.10 (10-GND), SN65LVDT41-X.2 (2-GND), SN65LVDT41-X.6 (6-GND), SN65LVDT41-X.10 (10-GND), SN65LVDT41-Y.2 (2-GND), SN65LVDT41-Y.6 (6-GND), SN65LVDT41-Y.10 (10-GND), SN65LVDT41-Z.2 (2-GND), SN65LVDT41-Z.6 (6-GND), SN65LVDT41-Z.10 (10-GND)
MISO1+A: CONN.74, SN65LVDT41-W.12 (12-5A)
MISO1-A: CONN.76, SN65LVDT41-W.11 (11-5B)
MOSI+A: CONN.70, SN65LVDT41-W.16 (16-3Y)
MOSI-A: CONN.72, SN65LVDT41-W.15 (15-3Z)
unnamed: ADUM4401-W.12 (12-VOC), SN65LVDT41-W.5 (5-3D)
unnamed: OMNETICS-CONNECTOR-SLAVE-W.B1 (CS-), SNDLVDT14-W.2 (2-1B)
unnamed: ADUM4401-W.11 (11-VID), SN65LVDT41-W.9 (9-5R)
unnamed: ADUM4401-W.13 (13-VOB), SN65LVDT41-W.3 (3-2D)
unnamed: ADUM4401-W.5 (5-VIC), SNDLVDT14-W.16 (16-3R)
unnamed: CONN.56, SN65LVDT41-X.11 (11-5B)
unnamed: ADUM4401-W.14 (14-VOA), SN65LVDT41-W.1 (1-1D)
unnamed: ADUM4401-W.3 (3-VIA), SNDLVDT14-W.20 (20-1R)
unnamed: ADUM4401-W.4 (4-VIB), SNDLVDT14-W.18 (18-2R)
unnamed: CONN.54, SN65LVDT41-X.12 (12-5A)
unnamed: ADUM4401-W.6 (6-VOD), SNDLVDT14-W.12 (12-5D)
unnamed: OMNETICS-CONNECTOR-SLAVE-W.T1 (CS+), SNDLVDT14-W.1 (1-1A)
unnamed: CONN.52, SN65LVDT41-X.15 (15-3Z)
unnamed: CONN.50, SN65LVDT41-X.16 (16-3Y)
unnamed: OMNETICS-CONNECTOR-SLAVE-W.T2 (+SCLK), SNDLVDT14-W.3 (3-2A)
unnamed: OMNETICS-CONNECTOR-SLAVE-W.B2 (-SCLK), SNDLVDT14-W.4 (4-2B)
unnamed: CONN.48, SN65LVDT41-X.17 (17-2Z)
unnamed: CONN.46, SN65LVDT41-X.18 (18-2Y)
unnamed: CONN.44, SN65LVDT41-X.19 (19-1Z)
unnamed: CONN.42, SN65LVDT41-X.20 (20-1Y)
unnamed: OMNETICS-CONNECTOR-SLAVE-X.T2 (+SCLK), SNDLVDT14-X.3 (3-2A)
unnamed: OMNETICS-CONNECTOR-SLAVE-X.B2 (-SCLK), SNDLVDT14-X.4 (4-2B)
unnamed: OMNETICS-CONNECTOR-SLAVE-X.T3 (+MOSI), SNDLVDT14-X.5 (5-3A)
unnamed: OMNETICS-CONNECTOR-SLAVE-X.B3 (-MOSI), SNDLVDT14-X.6 (6-3B)
unnamed: OMNETICS-CONNECTOR-SLAVE-X.T4 (+MISO1), SNDLVDT14-X.9 (9-5Y)
unnamed: OMNETICS-CONNECTOR-SLAVE-X.B4 (-MISO1), SNDLVDT14-X.10 (10-5Z)
unnamed: CONN.36, SN65LVDT41-Y.11 (11-5B)
unnamed: CONN.34, SN65LVDT41-Y.12 (12-5A)
unnamed: ADUM4401-X.14 (14-VOA), SN65LVDT41-X.1 (1-1D)
unnamed: CONN.32, SN65LVDT41-Y.15 (15-3Z)
unnamed: CONN.30, SN65LVDT41-Y.16 (16-3Y)
unnamed: ADUM4401-X.11 (11-VID), SN65LVDT41-X.9 (9-5R)
unnamed: CONN.28, SN65LVDT41-Y.17 (17-2Z)
unnamed: CONN.26, SN65LVDT41-Y.18 (18-2Y)
unnamed: C42.1, S1.2 (1), U$1.1 (IN)
unnamed: ADUM4401-X.6 (6-VOD), SNDLVDT14-X.12 (12-5D)
unnamed: OMNETICS-CONNECTOR-SLAVE-W.T3 (+MOSI), SNDLVDT14-W.5 (5-3A)
unnamed: OMNETICS-CONNECTOR-SLAVE-W.B3 (-MOSI), SNDLVDT14-W.6 (6-3B)
unnamed: OMNETICS-CONNECTOR-SLAVE-W.T4 (+MISO1), SNDLVDT14-W.9 (9-5Y)
unnamed: ADUM4401-X.5 (5-VIC), SNDLVDT14-X.16 (16-3R)
unnamed: ADUM4401-X.4 (4-VIB), SNDLVDT14-X.18 (18-2R)
unnamed: ADUM4401-X.3 (3-VIA), SNDLVDT14-X.20 (20-1R)
unnamed: OMNETICS-CONNECTOR-SLAVE-X.B1 (CS-), SNDLVDT14-X.2 (2-1B)
unnamed: OMNETICS-CONNECTOR-SLAVE-X.T1 (CS+), SNDLVDT14-X.1 (1-1A)
unnamed: ADUM4401-X.12 (12-VOC), SN65LVDT41-X.5 (5-3D)
unnamed: ADUM4401-X.13 (13-VOB), SN65LVDT41-X.3 (3-2D)
unnamed: CONN.24, SN65LVDT41-Y.19 (19-1Z)
unnamed: OMNETICS-CONNECTOR-SLAVE-W.B4 (-MISO1), SNDLVDT14-W.10 (10-5Z)
unnamed: CONN.22, SN65LVDT41-Y.20 (20-1Y)
unnamed: CONN.16, SN65LVDT41-Z.11 (11-5B)
unnamed: CONN.14, SN65LVDT41-Z.12 (12-5A)
unnamed: CONN.12, SN65LVDT41-Z.15 (15-3Z)
unnamed: CONN.10, SN65LVDT41-Z.16 (16-3Y)
unnamed: CONN.8, SN65LVDT41-Z.17 (17-2Z)
unnamed: CONN.6, SN65LVDT41-Z.18 (18-2Y)
unnamed: OMNETICS-CONNECTOR-SLAVE-Y.T2 (+SCLK), SNDLVDT14-Y.3 (3-2A)
unnamed: OMNETICS-CONNECTOR-SLAVE-Y.B2 (-SCLK), SNDLVDT14-Y.4 (4-2B)
unnamed: OMNETICS-CONNECTOR-SLAVE-Y.T3 (+MOSI), SNDLVDT14-Y.5 (5-3A)
unnamed: OMNETICS-CONNECTOR-SLAVE-Y.B3 (-MOSI), SNDLVDT14-Y.6 (6-3B)
unnamed: OMNETICS-CONNECTOR-SLAVE-Y.T4 (+MISO1), SNDLVDT14-Y.9 (9-5Y)
unnamed: OMNETICS-CONNECTOR-SLAVE-Y.B4 (-MISO1), SNDLVDT14-Y.10 (10-5Z)
unnamed: ADUM4401-Y.14 (14-VOA), SN65LVDT41-Y.1 (1-1D)
unnamed: ADUM4401-Y.11 (11-VID), SN65LVDT41-Y.9 (9-5R)
unnamed: ADUM4401-Y.6 (6-VOD), SNDLVDT14-Y.12 (12-5D)
unnamed: ADUM4401-Y.5 (5-VIC), SNDLVDT14-Y.16 (16-3R)
unnamed: ADUM4401-Y.4 (4-VIB), SNDLVDT14-Y.18 (18-2R)
unnamed: ADUM4401-Y.3 (3-VIA), SNDLVDT14-Y.20 (20-1R)
unnamed: OMNETICS-CONNECTOR-SLAVE-Y.B1 (CS-), SNDLVDT14-Y.2 (2-1B)
unnamed: OMNETICS-CONNECTOR-SLAVE-Y.T1 (CS+), SNDLVDT14-Y.1 (1-1A)
unnamed: ADUM4401-Y.12 (12-VOC), SN65LVDT41-Y.5 (5-3D)
unnamed: ADUM4401-Y.13 (13-VOB), SN65LVDT41-Y.3 (3-2D)
unnamed: CONN.4, SN65LVDT41-Z.19 (19-1Z)
unnamed: CONN.2, SN65LVDT41-Z.20 (20-1Y)
unnamed: OMNETICS-CONNECTOR-SLAVE-Z.T2 (+SCLK), SNDLVDT14-Z.3 (3-2A)
unnamed: OMNETICS-CONNECTOR-SLAVE-Z.B2 (-SCLK), SNDLVDT14-Z.4 (4-2B)
unnamed: OMNETICS-CONNECTOR-SLAVE-Z.T3 (+MOSI), SNDLVDT14-Z.5 (5-3A)
unnamed: OMNETICS-CONNECTOR-SLAVE-Z.B3 (-MOSI), SNDLVDT14-Z.6 (6-3B)
unnamed: OMNETICS-CONNECTOR-SLAVE-Z.T4 (+MISO1), SNDLVDT14-Z.9 (9-5Y)
unnamed: OMNETICS-CONNECTOR-SLAVE-Z.B4 (-MISO1), SNDLVDT14-Z.10 (10-5Z)
unnamed: ADUM4401-Z.14 (14-VOA), SN65LVDT41-Z.1 (1-1D)
unnamed: ADUM4401-Z.11 (11-VID), SN65LVDT41-Z.9 (9-5R)
unnamed: ADUM4401-Z.6 (6-VOD), SNDLVDT14-Z.12 (12-5D)
unnamed: ADUM4401-Z.5 (5-VIC), SNDLVDT14-Z.16 (16-3R)
unnamed: ADUM4401-Z.4 (4-VIB), SNDLVDT14-Z.18 (18-2R)
unnamed: ADUM4401-Z.3 (3-VIA), SNDLVDT14-Z.20 (20-1R)
unnamed: OMNETICS-CONNECTOR-SLAVE-Z.B1 (CS-), SNDLVDT14-Z.2 (2-1B)
unnamed: OMNETICS-CONNECTOR-SLAVE-Z.T1 (CS+), SNDLVDT14-Z.1 (1-1A)
unnamed: ADUM4401-Z.12 (12-VOC), SN65LVDT41-Z.5 (5-3D)
unnamed: ADUM4401-Z.13 (13-VOB), SN65LVDT41-Z.3 (3-2D)
SCLK+A: CONN.66, SN65LVDT41-W.18 (18-2Y)
SCLK-A: CONN.68, SN65LVDT41-W.17 (17-2Z)
VDD-3.3V: ADUM4401-W.1 (1-VDD1), ADUM4401-W.7 (7-VE1), ADUM4401-X.1 (1-VDD1), ADUM4401-X.7 (7-VE1), ADUM4401-Y.1 (1-VDD1), ADUM4401-Y.7 (7-VE1), ADUM4401-Z.1 (1-VDD1), ADUM4401-Z.7 (7-VE1), ADUM6000-W.1 (1-VDD1), ADUM6000-W.6 (6-RCSEL), ADUM6000-W.7 (7-VDD1), ADUM6000-X.1 (1-VDD1), ADUM6000-X.6 (6-RCSEL), ADUM6000-X.7 (7-VDD1), ADUM6000-Y.1 (1-VDD1), ADUM6000-Y.6 (6-RCSEL), ADUM6000-Y.7 (7-VDD1), ADUM6000-Z.1 (1-VDD1), ADUM6000-Z.6 (6-RCSEL), ADUM6000-Z.7 (7-VDD1), C1.2, C2.2, C5.1, C8.1, C9.2, C10.2, C14.1, C15.2, C16.2, C20.1, C21.2, C22.2, C27.1, C28.1, C31.1, C32.1, C35.1, C36.1, C39.1, C40.1, C41.2, S2.2 (1), SNDLVDT14-W.17 (17-VCC), SNDLVDT14-X.17 (17-VCC), SNDLVDT14-Y.17 (17-VCC), SNDLVDT14-Z.17 (17-VCC), U$1.3 (OUT)
VDD-ISO-1: ADUM4401-W.10 (10-VE2), ADUM4401-W.16 (16-VDD2), ADUM6000-W.10 (10-VISO), ADUM6000-W.16 (16-VISO), C3.2, C4.2, C6.1, C37.1, C38.1, CONN.78, SN65LVDT41-W.4 (4-VCC)
VDD-ISO-2: ADUM4401-X.10 (10-VE2), ADUM4401-X.16 (16-VDD2), ADUM6000-X.10 (10-VISO), ADUM6000-X.16 (16-VISO), C7.1, C11.2, C12.2, C33.1, C34.1, CONN.58, SN65LVDT41-X.4 (4-VCC)
VDD-ISO-3: ADUM4401-Y.10 (10-VE2), ADUM4401-Y.16 (16-VDD2), ADUM6000-Y.10 (10-VISO), ADUM6000-Y.16 (16-VISO), C13.1, C17.2, C18.2, C29.1, C30.1, CONN.38, SN65LVDT41-Y.4 (4-VCC)
VDD-ISO-4: ADUM4401-Z.10 (10-VE2), ADUM4401-Z.16 (16-VDD2), ADUM6000-Z.10 (10-VISO), ADUM6000-Z.16 (16-VISO), C19.1, C23.2, C24.2, C25.1, C26.1, CONN.18, SN65LVDT41-Z.4 (4-VCC)

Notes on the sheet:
RHD Isolator Board
Iso Power
Eval Side
Iso Side

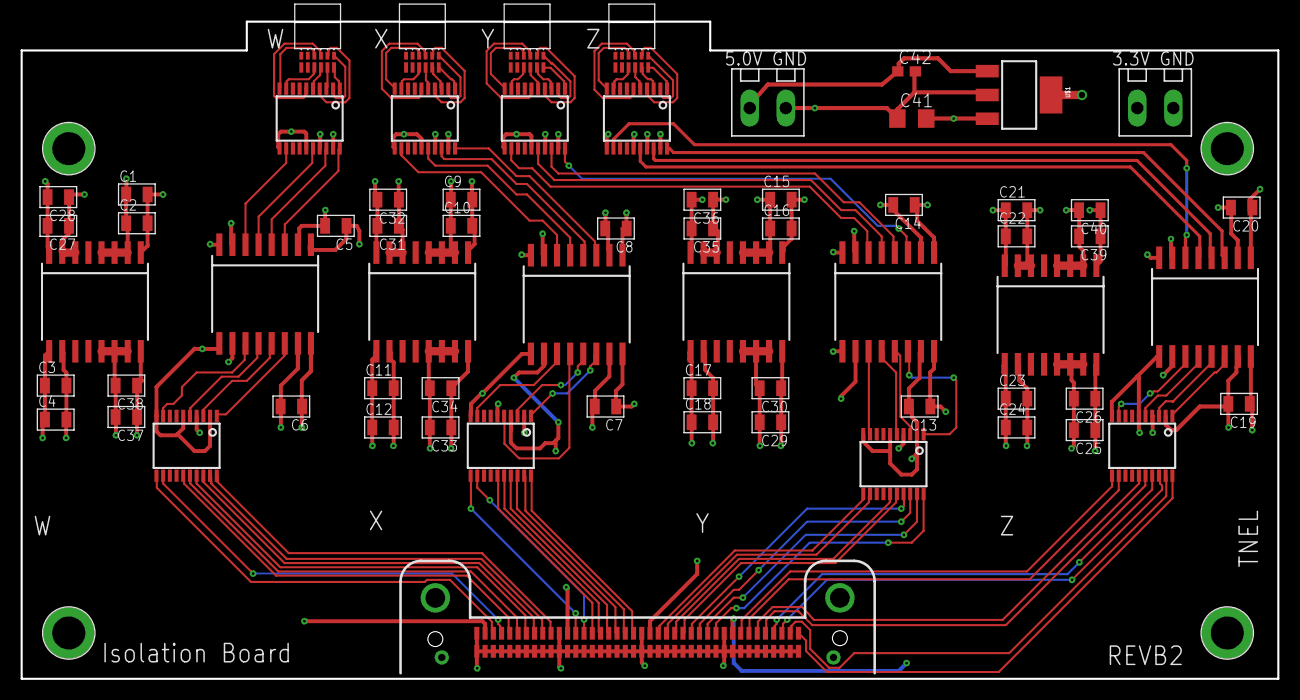
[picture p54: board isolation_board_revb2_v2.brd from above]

Board: 4 copper layers, 121.9 x 63.8 mm, 70 parts (0 on the bottom side), 104 nets.

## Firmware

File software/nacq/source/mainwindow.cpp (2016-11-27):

//  ------------------------------------------------------------------------
//
//  This file is part of the Intan Technologies RHD2000 Interface
//  Version 1.5
//  Copyright (C) 2013-2016 Intan Technologies
//
//  ------------------------------------------------------------------------
//
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
#include <QtGui>
#include <QWidget>
#include <QFile>
#include <QTime>
//#include <QSound>
#include <iostream>
#include <fstream>
#include <vector>
#include <queue>

#include "qtincludes.h"

#include "mainwindow.h"
#include "globalconstants.h"
#include "signalprocessor.h"
#include "waveplot.h"
#include "signalsources.h"
#include "signalgroup.h"
#include "signalchannel.h"
#include "bandwidthdialog.h"
#include "impedancefreqdialog.h"
#include "renamechanneldialog.h"
#include "keyboardshortcutdialog.h"
#include "helpdialogchipfilters.h"
#include "helpdialogcomparators.h"
#include "helpdialogdacs.h"
#include "helpdialoghighpassfilter.h"
#include "helpdialognotchfilter.h"
#include "helpdialogfastsettle.h"
#include "spikescopedialog.h"
#include "triggerrecorddialog.h"
#include "setsaveformatdialog.h"
#include "auxdigoutconfigdialog.h"
#include "cabledelaydialog.h"
#include "rhd2000evalboard.h"
#include "rhd2000evalboard.h"
#include "rhd2000registers.h"
#include "rhd2000datablock.h"
#include "okFrontPanelDLL.h"

// Main Window of RHD2000 USB interface application.

// Constructor.
MainWindow::MainWindow()
{
    // Default amplifier bandwidth settings
    desiredLowerBandwidth = 0.1;
    desiredUpperBandwidth = 7500.0;
    desiredDspCutoffFreq = 1.0;
    dspEnabled = true;

    // Default electrode impedance measurement frequency
    desiredImpedanceFreq = 1000.0;

    actualImpedanceFreq = 0.0;
    impedanceFreqValid = false;

    // Set up vectors for 8 DACs on USB interface board
    dacEnabled.resize(8);
    dacEnabled.fill(false);
    dacSelectedChannel.resize(8);
    dacSelectedChannel.fill(0);

    cableLengthPortA = 1.0;
    cableLengthPortB = 1.0;
    cableLengthPortC = 1.0;
    cableLengthPortD = 1.0;

    chipId.resize(MAX_NUM_DATA_STREAMS);
    chipId.fill(-1);

    for (int i = 0; i < 16; ++i) {
        ttlOut[i] = 0;
    }
    evalBoardMode = 0;

    // Set dialog pointers to null.
    spikeScopeDialog = 0;
    keyboardShortcutDialog = 0;
    helpDialogChipFilters = 0;
    helpDialogComparators = 0;
    helpDialogDacs = 0;
    helpDialogHighpassFilter = 0;
    helpDialogNotchFilter = 0;
    helpDialogFastSettle = 0;

    recordTriggerChannel = 0;
    recordTriggerPolarity = 0;
    recordTriggerBuffer = 1;
    postTriggerTime = 1;
    saveTriggerChannel = true;

    signalSources = new SignalSources();

    channelVisible.resize(MAX_NUM_DATA_STREAMS);
    for (int i = 0; i < MAX_NUM_DATA_STREAMS; ++i) {
        channelVisible[i].resize(32);
        channelVisible[i].fill(false);
    }

    signalProcessor = new SignalProcessor();
    notchFilterFrequency = 60.0;
    notchFilterBandwidth = 10.0;
    notchFilterEnabled = false;
    signalProcessor->setNotchFilterEnabled(notchFilterEnabled);
    highpassFilterFrequency = 250.0;
    highpassFilterEnabled = false;
    signalProcessor->setHighpassFilterEnabled(highpassFilterEnabled);

    running = false;
    recording = false;
    triggerSet = false;
    triggered = false;

    saveTemp = false;
    saveTtlOut = false;
    validFilename = false;
    synthMode = false;
    fastSettleEnabled = false;

    wavePlot = new WavePlot(signalProcessor, signalSources, this, this);

    connect(wavePlot, SIGNAL(selectedChannelChanged(SignalChannel*)),
            this, SLOT(newSelectedChannel(SignalChannel*)));

    createActions();
    createMenus();
    createStatusBar();
    createLayout();

    recordButton->setEnabled(validFilename);
    triggerButton->setEnabled(validFilename);
    stopButton->setEnabled(false);

    manualDelayEnabled.resize(4);
    manualDelayEnabled.fill(false);
    manualDelay.resize(4);
    manualDelay.fill(0);

    openInterfaceBoard();

    changeSampleRate(sampleRateComboBox->currentIndex());
    sampleRateComboBox->setCurrentIndex(14);

    scanPorts();
    setStatusBarReady();

    if (!synthMode) {
        setDacThreshold1(0);
        setDacThreshold2(0);
        setDacThreshold3(0);
        setDacThreshold4(0);
        setDacThreshold5(0);
        setDacThreshold6(0);
        setDacThreshold7(0);
        setDacThreshold8(0);

        evalBoard->enableDacHighpassFilter(false);
        evalBoard->setDacHighpassFilter(250.0);
    }

    auxDigOutEnabled.resize(4);
    auxDigOutEnabled.fill(false);
    auxDigOutChannel.resize(4);
    auxDigOutChannel.fill(0);
    updateAuxDigOut();

    // Default data file format.
    setSaveFormat(SaveFormatIntan);
    newSaveFilePeriodMinutes = 1;

    // Default settings for display scale combo boxes.
    yScaleComboBox->setCurrentIndex(3);
    tScaleComboBox->setCurrentIndex(4);

    changeTScale(tScaleComboBox->currentIndex());
    changeYScale(yScaleComboBox->currentIndex());

    // QSound cannot play wav files directly from Qt resource files, so
    // this is a workaround:  Copy the wav file from the resource file to
    // a temporary directory, then play it from there when needed.
    QFile fileTemp(QDir::tempPath() + "/triggerbeep.wav");
    if (fileTemp.open(QIODevice::ReadWrite))
    {
        QFile resourceFile(":/sounds/triggerbeep.wav");
        if(resourceFile.open(QIODevice::ReadOnly))
        {
            fileTemp.write(resourceFile.readAll());
            resourceFile.close();
        }
        fileTemp.close();
    }

    QFile fileTemp2(QDir::tempPath() + "/triggerendbeep.wav");
    if (fileTemp2.open(QIODevice::ReadWrite))
    {
        QFile resourceFile2(":/sounds/triggerendbeep.wav");
        if(resourceFile2.open(QIODevice::ReadOnly))
        {
            fileTemp2.write(resourceFile2.readAll());
            resourceFile2.close();
        }
        fileTemp2.close();
    }
}

// Scan SPI Ports A-D to identify all connected RHD2000 amplifier chips.
void MainWindow::scanPorts()
{
    statusBar()->showMessage("Scanning ports...");

    // Scan SPI Ports.
    findConnectedAmplifiers();

    // Configure SignalProcessor object for the required number of data streams.
    if (!synthMode) {
        signalProcessor->allocateMemory(evalBoard->getNumEnabledDataStreams());
        setWindowTitle(tr("Intan Technologies RHD2000 Interface"));
    } else {
        signalProcessor->allocateMemory(1);
        setWindowTitle(tr("Intan Technologies RHD2000 Interface "
                          "(Demonstration Mode with Synthesized Biopotentials)"));
    }

    // Turn on appropriate (optional) LEDs for Ports A-D
    if (!synthMode) {
        ttlOut[11] = 0;
        ttlOut[12] = 0;
        ttlOut[13] = 0;
        ttlOut[14] = 0;
        if (signalSources->signalPort[0].enabled) {
            ttlOut[11] = 1;
        }
        if (signalSources->signalPort[1].enabled) {
            ttlOut[12] = 1;
        }
        if (signalSources->signalPort[2].enabled) {
            ttlOut[13] = 1;
        }
        if (signalSources->signalPort[3].enabled) {
            ttlOut[14] = 1;
        }
        evalBoard->setTtlOut(ttlOut);
    }

    // Switch display to the first port that has an amplifier connected.
    if (signalSources->signalPort[0].enabled) {
        wavePlot->initialize(0);
    } else if (signalSources->signalPort[1].enabled) {
        wavePlot->initialize(1);
    } else if (signalSources->signalPort[2].enabled) {
        wavePlot->initialize(2);
    } else if (signalSources->signalPort[3].enabled) {
        wavePlot->initialize(3);
    } else {
        wavePlot->initialize(4);
        QMessageBox::information(this, tr("No RHD2000 Amplifiers Detected"),
                tr("No RHD2000 amplifiers are connected to the interface board."
                   "<p>Connect amplifier modules and click 'Rescan Ports A-D' under "
                   "the Configure tab."
                   "<p>You may record from analog and digital inputs on the evaluation "
                   "board in the absence of amplifier modules."));
    }

    wavePlot->setSampleRate(boardSampleRate);
    changeTScale(tScaleComboBox->currentIndex());
    changeYScale(yScaleComboBox->currentIndex());

    statusBar()->clearMessage();
}
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

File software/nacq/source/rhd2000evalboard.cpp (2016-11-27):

//----------------------------------------------------------------------------------
// rhd2000evalboard.cpp
//
// Intan Technoloies RHD2000 Rhythm Interface API
// Rhd2000EvalBoard Class
// Version 1.5 (25 April 2016)
//
// Copyright (c) 2013-2016 Intan Technologies LLC
//
// This software is provided 'as-is', without any express or implied warranty.
// In no event will the authors be held liable for any damages arising from the
// use of this software.
//
// Permission is granted to anyone to use this software for any applications that
// use Intan Technologies integrated circuits, and to alter it and redistribute it
// freely.
//
// See http://www.intantech.com for documentation and product information.
//----------------------------------------------------------------------------------

#include <iostream>
#include <iomanip>
#include <fstream>
#include <vector>
#include <queue>
#include <cmath>

#include "rhd2000evalboard.h"
#include "rhd2000datablock.h"

#include "okFrontPanelDLL.h"

using namespace std;

// This class provides access to and control of the Opal Kelly XEM6010 USB/FPGA
// interface board running the Rhythm interface Verilog code.

// Constructor.  Set sampling rate variable to 30.0 kS/s/channel (FPGA default).
Rhd2000EvalBoard::Rhd2000EvalBoard()
{
    int i;
    sampleRate = SampleRate30000Hz; // Rhythm FPGA boots up with 30.0 kS/s/channel sampling rate
    numDataStreams = 0;

    for (i = 0; i < MAX_NUM_DATA_STREAMS; ++i) {
        dataStreamEnabled[i] = 0;
    }

    cableDelay.resize(4, -1);
}

// Find an Opal Kelly XEM6010-LX45 board attached to a USB port and open it.
// Returns 1 if successful, -1 if FrontPanel cannot be loaded, and -2 if XEM6010 can't be found.
int Rhd2000EvalBoard::open()
{
    char dll_date[32], dll_time[32];
    string serialNumber = "";
    int i, nDevices;

    cout << "---- Intan Technologies ---- Rhythm RHD2000 Controller v1.0 ----" << endl << endl;
    if (okFrontPanelDLL_LoadLib(NULL) == false) {
        cerr << "FrontPanel DLL could not be loaded.  " <<
                "Make sure this DLL is in the application start directory." << endl;
        return -1;
    }
    okFrontPanelDLL_GetVersion(dll_date, dll_time);
    cout << endl << "FrontPanel DLL loaded.  Built: " << dll_date << "  " << dll_time << endl;

    dev = new okCFrontPanel;

    cout << endl << "Scanning USB for Opal Kelly devices..." << endl << endl;
    nDevices = dev->GetDeviceCount();
    cout << "Found " << nDevices << " Opal Kelly device" << ((nDevices == 1) ? "" : "s") <<
            " connected:" << endl;
    for (i = 0; i < nDevices; ++i) {
        cout << "  Device #" << i + 1 << ": Opal Kelly " <<
                opalKellyModelName(dev->GetDeviceListModel(i)).c_str() <<
                " with serial number " << dev->GetDeviceListSerial(i).c_str() << endl;
    }
    cout << endl;

    // Find first device in list of type XEM6010LX45.
    for (i = 0; i < nDevices; ++i) {
        if (dev->GetDeviceListModel(i) == OK_PRODUCT_XEM6010LX45) {
            serialNumber = dev->GetDeviceListSerial(i);
            break;
        }
    }

    cout << "Attempting to connect to device '" << serialNumber.c_str() << "'\n";

    okCFrontPanel::ErrorCode result = dev->OpenBySerial(serialNumber);
    // Attempt to open device.
    if (result != okCFrontPanel::NoError) {
        delete dev;
        cerr << "Device could not be opened.  Is one connected?" << endl;
        cerr << "Error = " << result << "\n";
        return -2;
    }

    // Configure the on-board PLL appropriately.
    dev->LoadDefaultPLLConfiguration();

    // Get some general information about the XEM.
    cout << "FPGA system clock: " << getSystemClockFreq() << " MHz" << endl; // Should indicate 100 MHz
    cout << "Opal Kelly device firmware version: " << dev->GetDeviceMajorVersion() << "." <<
            dev->GetDeviceMinorVersion() << endl;
    cout << "Opal Kelly device serial number: " << dev->GetSerialNumber().c_str() << endl;
    cout << "Opal Kelly device ID string: " << dev->GetDeviceID().c_str() << endl << endl;

    return 1;
}

// Uploads the configuration file (bitfile) to the FPGA.  Returns true if successful.
bool Rhd2000EvalBoard::uploadFpgaBitfile(string filename)
{
    okCFrontPanel::ErrorCode errorCode = dev->ConfigureFPGA(filename);

    switch (errorCode) {
        case okCFrontPanel::NoError:
            break;
        case okCFrontPanel::DeviceNotOpen:
            cerr << "FPGA configuration failed: Device not open." << endl;
            return(false);
        case okCFrontPanel::FileError:
            cerr << "FPGA configuration failed: Cannot find configuration file." << endl;
            return(false);
        case okCFrontPanel::InvalidBitstream:
            cerr << "FPGA configuration failed: Bitstream is not properly formatted." << endl;
            return(false);
        case okCFrontPanel::DoneNotHigh:
            cerr << "FPGA configuration failed: FPGA DONE signal did not assert after configuration." << endl;
            return(false);
        case okCFrontPanel::TransferError:
            cerr << "FPGA configuration failed: USB error occurred during download." << endl;
            return(false);
        case okCFrontPanel::CommunicationError:
            cerr << "FPGA configuration failed: Communication error with firmware." << endl;
            return(false);
        case okCFrontPanel::UnsupportedFeature:
            cerr << "FPGA configuration failed: Unsupported feature." << endl;
            return(false);
        default:
            cerr << "FPGA configuration failed: Unknown error." << endl;
            return(false);
    }

    // Check for Opal Kelly FrontPanel support in the FPGA configuration.
    if (dev->IsFrontPanelEnabled() == false) {
        cerr << "Opal Kelly FrontPanel support is not enabled in this FPGA configuration." << endl;
        delete dev;
        return(false);
    }

    int boardId, boardVersion;
    dev->UpdateWireOuts();
    boardId = dev->GetWireOutValue(WireOutBoardId);
    boardVersion = dev->GetWireOutValue(WireOutBoardVersion);

    if (boardId != RHYTHM_BOARD_ID) {
        cerr << "FPGA configuration does not support Rhythm.  Incorrect board ID: " << boardId << endl;
        return(false);
    } else {
        cout << "Rhythm configuration file successfully loaded.  Rhythm version number: " <<
                boardVersion << endl << endl;
    }

    return(true);
}
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

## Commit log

2016-03-14 Initial Commit - Includes Isolation, Easy and Flex PCBs and executable software. Coming soon source software, case design files and more documentation
    [easy_connector_v5_auto.brd, easy_connector_v5_auto.sch, easy_connector_v5_auto_bom.xls, easy_connector_v5_auto_centroid.csv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]
2016-03-16 Uploading easy board, intan headstage, and nacq enclosure design files. File format are provided in solidworks and .stl formats
    [A79623-001.SLDPRT, Assem1.SLDASM, Assem2.SLDASM, Body1.STL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]
2016-07-04 Moved flex adapter board design files to 'Flex Adapter' directory
    [FFC_Omnetics64_0a8.brd, FFC_Omnetics64_0a8.sch]
2016-11-01 Uploading (1) Pigtail Adapter Case and (2) Doucmentation for Flex Adapter
    [A79623-001.SLDPRT, A79623-001.STEP, Board.sldprt, Board_1.sldprt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]
2016-11-27 Updated Flex Adapter to be compatible with OSH Park and incorporated Intan's software upgrade v1.5 into system
    [BOM.xlsx, FFC_Omnetics64_0a8.brd, FFC_Omnetics64_0a8.sch, FFC_Omnetics64_0a9.brd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]
2017-04-20 Updated Flex Adapter Documentation to include full channel map
    [channel_map_spreadsheet.xlsx]
2017-12-02 Uploading ORH128 docs and files.
    [BOM_PartType-ORH128-Final v2-checklist.xlsx, BOM_PartType-ORH128-Final v2.xlsx, ORH128.step, ORH128_Electrode_Map.xlsx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]
2017-12-19 Case for ORH128 board
    [ORH128_Electrode_Map.xlsx, case128a.STL, case128aTOP.STL, case128v2.STL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]

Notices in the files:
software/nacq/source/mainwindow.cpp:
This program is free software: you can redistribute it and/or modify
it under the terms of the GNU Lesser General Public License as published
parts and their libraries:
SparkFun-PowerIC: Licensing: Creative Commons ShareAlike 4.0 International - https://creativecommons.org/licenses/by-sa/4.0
